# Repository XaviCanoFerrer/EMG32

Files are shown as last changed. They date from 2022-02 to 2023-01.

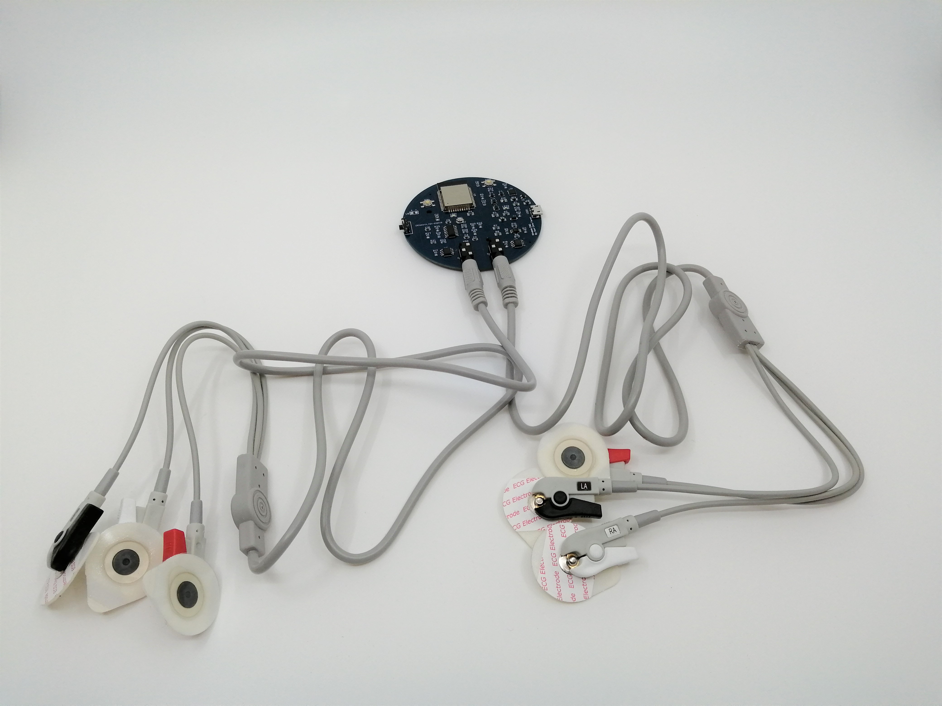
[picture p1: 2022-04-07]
IMG_20220404_123524.jpg

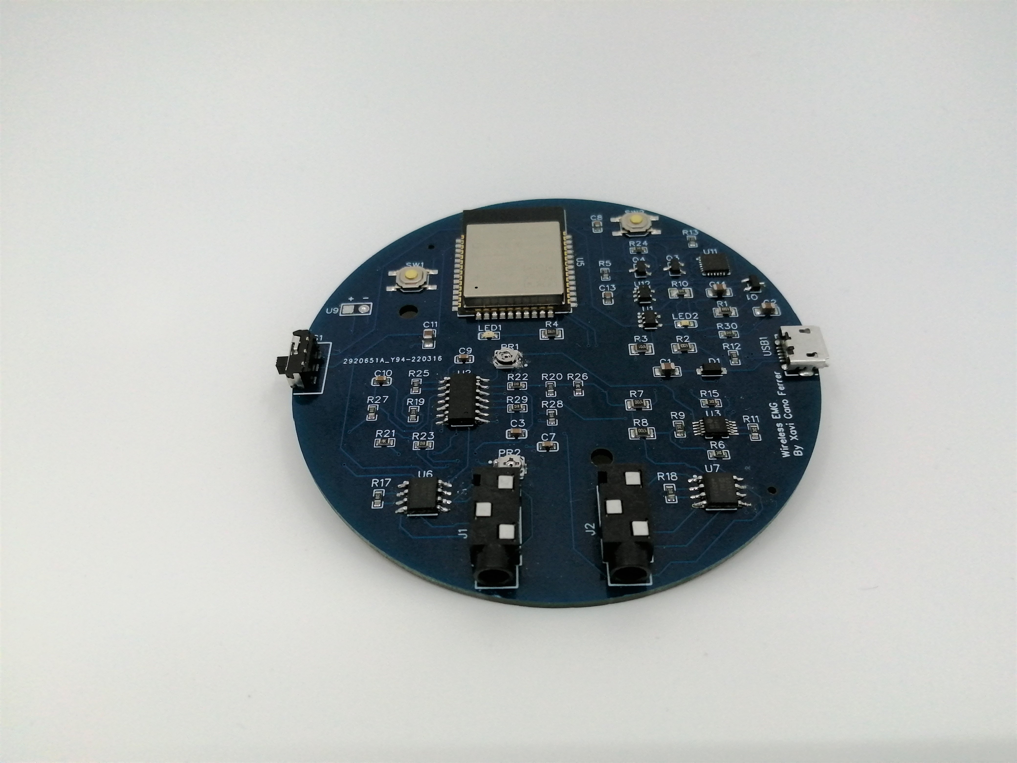
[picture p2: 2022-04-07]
IMG_20220404_123702.jpg

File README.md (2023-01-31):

# EMG32

Two-channel EMG acquisition system

# Features:

Adjustable total gain 100-10000

Instrumentation amplifier (AD8226)

12 bit ADC (Texas instruments ADS1015)

First order high and low pass filters fc = 22 Hz and fc = 482 Hz

LiPo battery power management system (It can be charged from the USB port)

The basic code has two modes, 2ch and 1 ch modes which can be selected pressing the SW1 pushbutton.

SW2 to reset the board.

Sampling frequencies 385 Hz through the serial port and 200 Hz using BT for 1 channel so not enough for sEMG standards Fs = 1kHz. 

It is still usable to measure muscle activity (RMS, how much and when) but not for frequency dependant processing or analysis as is shown in the single contraction spectrum:

<p align="center">
  
</p>

# V1 has a couple of mistakes but it can be fuctional: 

The quad amplifier (LM324) has to be assembled with a 180 degree rotation if not it will be shorted.

The JAC connectors are not close enough to the edge and depensing on the length of your cable it won't go deep enough to make a good contact.

Both mistakes are solved in V2.



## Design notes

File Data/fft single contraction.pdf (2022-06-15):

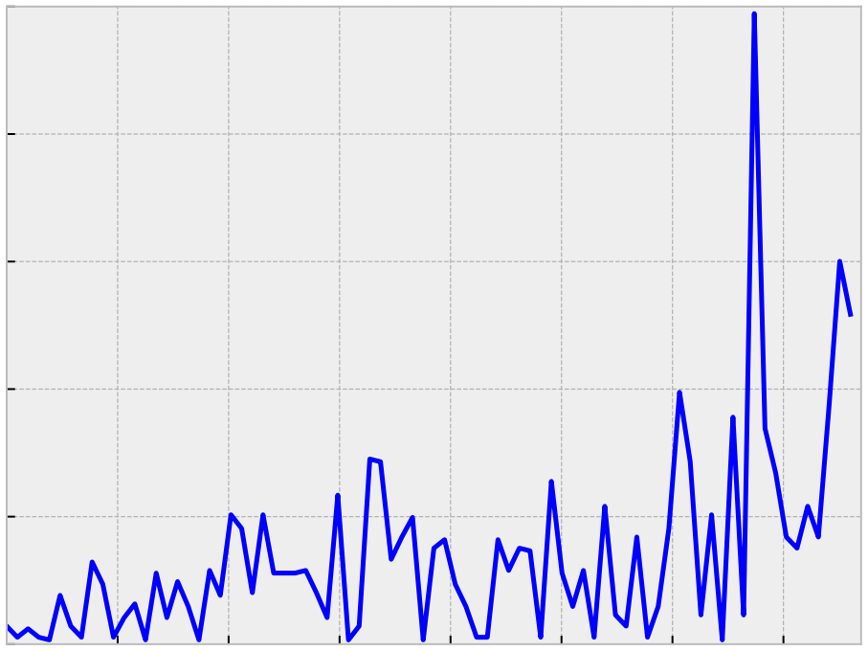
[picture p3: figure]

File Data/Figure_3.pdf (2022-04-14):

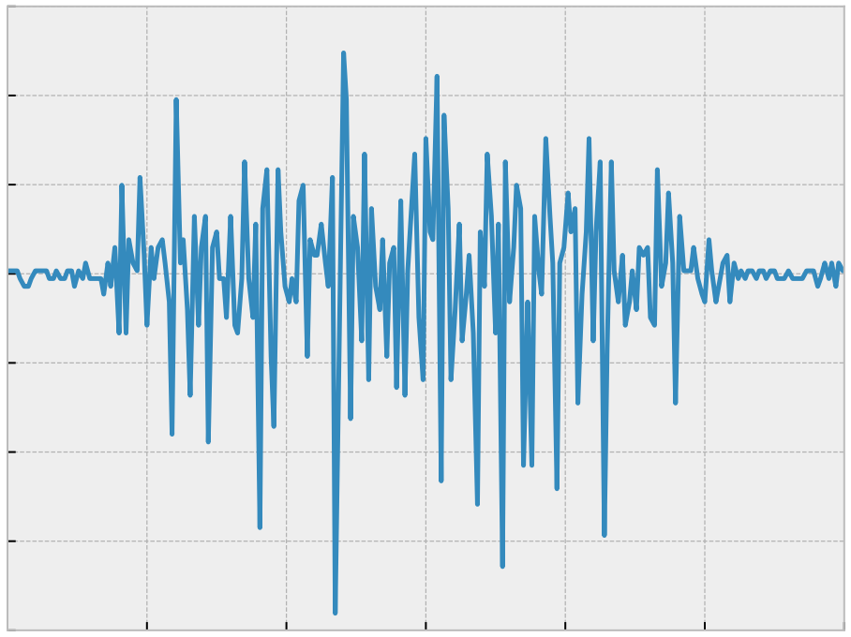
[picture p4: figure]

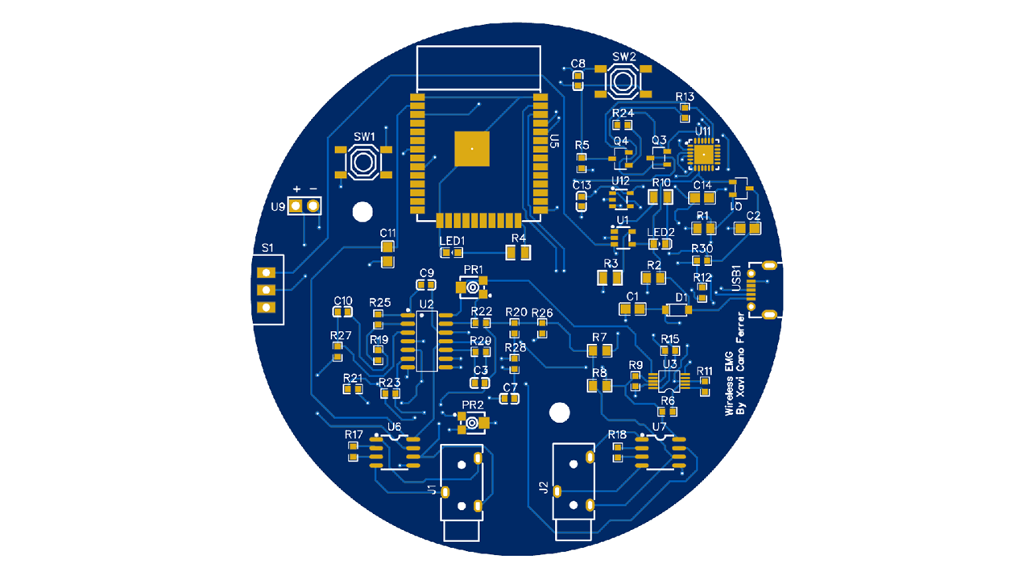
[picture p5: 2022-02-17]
Wireless EMG .png

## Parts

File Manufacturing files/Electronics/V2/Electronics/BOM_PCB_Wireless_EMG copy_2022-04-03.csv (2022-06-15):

ID | Name | Designator | Footprint | Quantity | Manufacturer Part | Manufacturer | Supplier | Supplier Part | Price | JLCPCB Part Class | LCSC Assembly
1 | LED-0603_G | LED1 | LED0603_GREEN | 1 | 0805G (Green) | KENTO | LCSC | C2297
2 | LM324 | U2 | SOIC-14_L8.7-W3.9-P1.27-LS6.0-BL | 1 | LM324 | PUOLOP | LCSC | C351427 | 0.143 | Extended Part
3 | AP7365-33WG-7 | U4 | SOT-25_L3.0-W1.6-P0.95-LS2.8-BR | 1 | AP7365-33WG-7 | DIODES | LCSC | C150742 | 0.229 | Extended Part
4 | 0.33uF | C3,C10 | C0603 | 2 | 0603B334K250NT | FH | LCSC | C1615 | 0.012
5 | 0.47uF | C7,C9 | C0603 | 2 | CL10B474KA8NNNC | SAMSUNG | LCSC | C1623 | 0.007
6 | 1uF | C8,C13 | C0603 | 2 | CL10A105KB8NNNC | SAMSUNG | LCSC | C15849 | 0.005
7 | 100 | R4 | R0805 | 1 | RC0805JR-07100RL | YAGEO | LCSC | C106949 | 0.002 |  | Yes
8 | 270 | R10 | R0805 | 1 | 0805W8F2700T5E | UniOhm | LCSC | C17590 | 0.003 |  | Yes
9 | 10uF | C1,C2,C14,C11 | C0805 | 4 | CL21A106KAYNNNE | SAMSUNG | LCSC | C15850 |  | Basic Part
10 | MBR120LSF | D1 | SOD-123_L2.8-W1.8-LS3.7-RD | 1 | MBR120LSF | SK | LCSC | C130880 | 0.035 | Extended Part
11 | Black headphone jack | J1,J2 | AUDIO-TH_PJ-3200 | 2 | Black headphone jack | BOOMELE | LCSC | C18166 | 0.049 | Extended Part
12 | LED-0603_R | LED2 | LED0603_RED | 1 | FC-2012HRK-620D | NATIONSTAR | LCSC | C84256 | 0.014
13 | 100K | PR1,PR2 | RES-ADJ-SMD_EVM3ESX50B25 | 2 | 0603WAF1003T5E | UniOhm | LCSC | C25803 | 0.001 | Extended Part
14 | DMG3415UQ-7 | Q1 | SOT-23-3_L2.9-W1.6-P1.90-LS2.8-BR | 1 | DMG3415U-7 | Diodes Incorporated | LCSC | C96616 | 0.666 | Extended Part
15 | MMBT2222A-G | Q3,Q4 | SOT-23-3_L2.9-W1.6-P1.90-LS2.8-BR | 2 | MMBT2222A-G | CJ | LCSC | C164898 | 0.021 | Extended Part
16 | 100K | R1,R2 | R0805 | 2 | RC0805FR-07100KL | YAGEO | LCSC | C96346 | 0.003 | Basic Part
17 | 470R | R7,R8 | R0805 | 2 | 0805W8F4700T5E | UniOhm | LCSC | C17710 | 0.002 | Basic Part
18 | 4.7k | R3 | R0805 | 1 | RMC08054.7K1%N | Tyohm | LCSC | C269746 | 0.006 |  | Yes
19 | 10k | R5,R6,R9,R11,R13,R15,R24 | R0603 | 7 | RMC060310K1%N | Tyohm | LCSC | C269701 | 0.004
20 | 100k | R12,R30 | R0603 | 2 | 0603WAF1003T5E | UniOhm | LCSC | C25803 | 0.001
21 | 1k | R17,R18,R19,R20,R22,R23,R25,R27,R28,R29 | R0603 | 10 | 0603WAF1001T5E | UniOhm | LCSC | C21190 | 0.001
22 | 15k | R21,R26 | R0603 | 2 | CR0603FA1502G | LIZ | LCSC | C100780 | 0.001
23 | TL32PO | S1 | TL3XPO | 1
24 | TS-1187A-B-A-B | SW2,SW1 | SW-SMD_4P-L5.1-W5.1-P3.70-LS6.5-TL-2 | 2 | TS-1187A-B-A-B | XKB Enterprise | LCSC | C318884 | 0.016 | Extended Part
25 | MCP73831T-2ACI/OT | U1 | SOT-23-5_L3.0-W1.7-P0.95-LS2.8-BR | 1 | MCP73831T-2ACI/OT | Microchip Tech | LCSC | C424093 | 0.949 | Extended Part
26 | ADS1015QDGSRQ1 | U3 | VSSOP-10_L3.0-W3.0-P0.50-LS4.9-BL | 1 | ADS1015QDGSRQ1 | Texas Instruments | LCSC | C201686 | 3.652 | Extended Part
27 | ESP32-WROOM-32D(16MB) | U5 | WIFIM-SMD_39P-L25.5-W18.0-P1.27-BL | 1 | ESP32-WROOM-32D | ESPRESSIF 乐鑫 | LCSC | C473012 | 3.751 | Extended Part
28 | AD8226ARZ | U6,U7 | SOIC-8_L5.0-W4.0-P1.27-LS6.0-BL | 2 | AD8226ARZ | ADI | LCSC | C34250 | 4.68 | Extended Part
29 | CP2104-F03-GM | U11 | QFN-24_L4.0-W4.0-P0.50-BL-EP2.7 | 1 | CP2104-F03-GM | SILICON LABS | LCSC | C47742 | 4.169 | Basic Part
30 | micro USBFemale | USB1 | MICRO-USB-SMD_5P-P0.65-H-F_C10418 | 1 | micro USBFemale | ValuePro | LCSC | C10418 | 0.065 | Extended Part
31 | 54102-T0600LF | U9 | HDR-TH_2P-P2.54-V-M-R2-C1-S2.54 | 1 | 54102-T0600LF | Amphenol ICC | LCSC | C213465 | 0.018

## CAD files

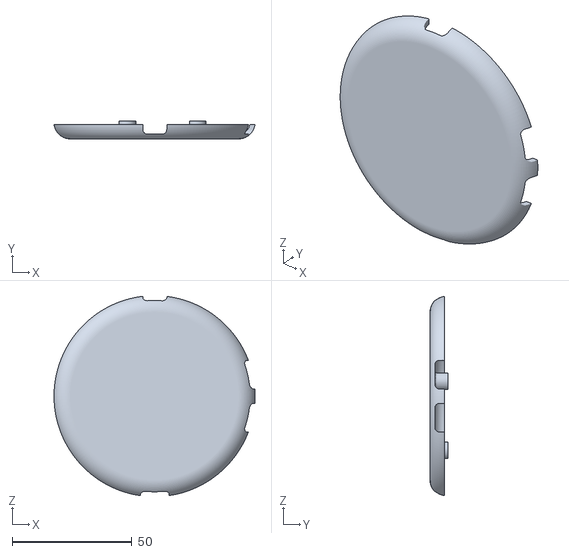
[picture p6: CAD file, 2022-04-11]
Manufacturing files/Case/Case top (Without holes for LED).stl
84.0 x 7.50 x 83.3

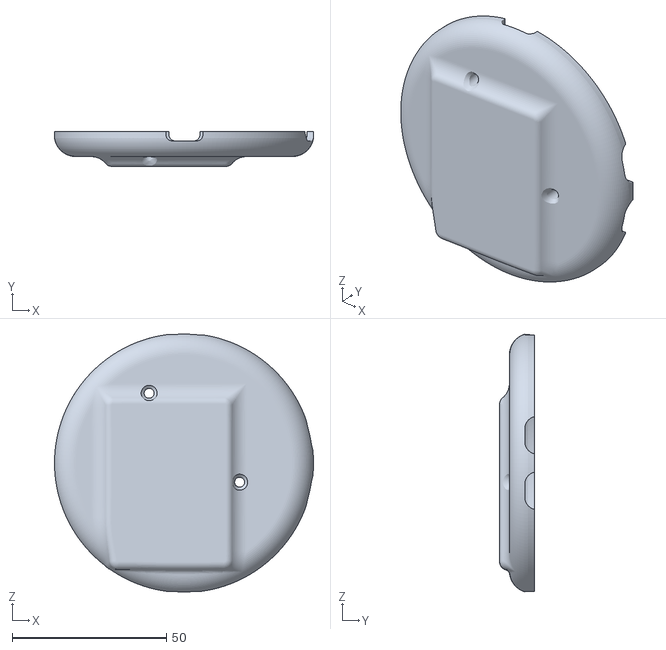
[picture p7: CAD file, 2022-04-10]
Manufacturing files/Case/Case bottom V2.stl
84.0 x 11.3 x 83.6

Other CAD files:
Manufacturing files/Case/Case top.stl
Design files/Case/Case assembly.iam
Design files/Case/Case bottom V2.ipt
Design files/Case/Case bottom.ipt
Design files/Case/Case top.ipt
Design files/Case/OldVersions/Case assembly.0003.iam
Design files/Case/OldVersions/Case top.0010.ipt
Design files/OldVersions/Case assembly.0002.iam
Design files/OldVersions/Case bottom V2.0009.ipt
Design files/OldVersions/Case bottom.0009.ipt
Design files/OldVersions/Case top.0009.ipt

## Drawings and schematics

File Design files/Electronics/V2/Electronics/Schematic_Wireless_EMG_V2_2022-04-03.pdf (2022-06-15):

## Power supply

## USB to serial converter

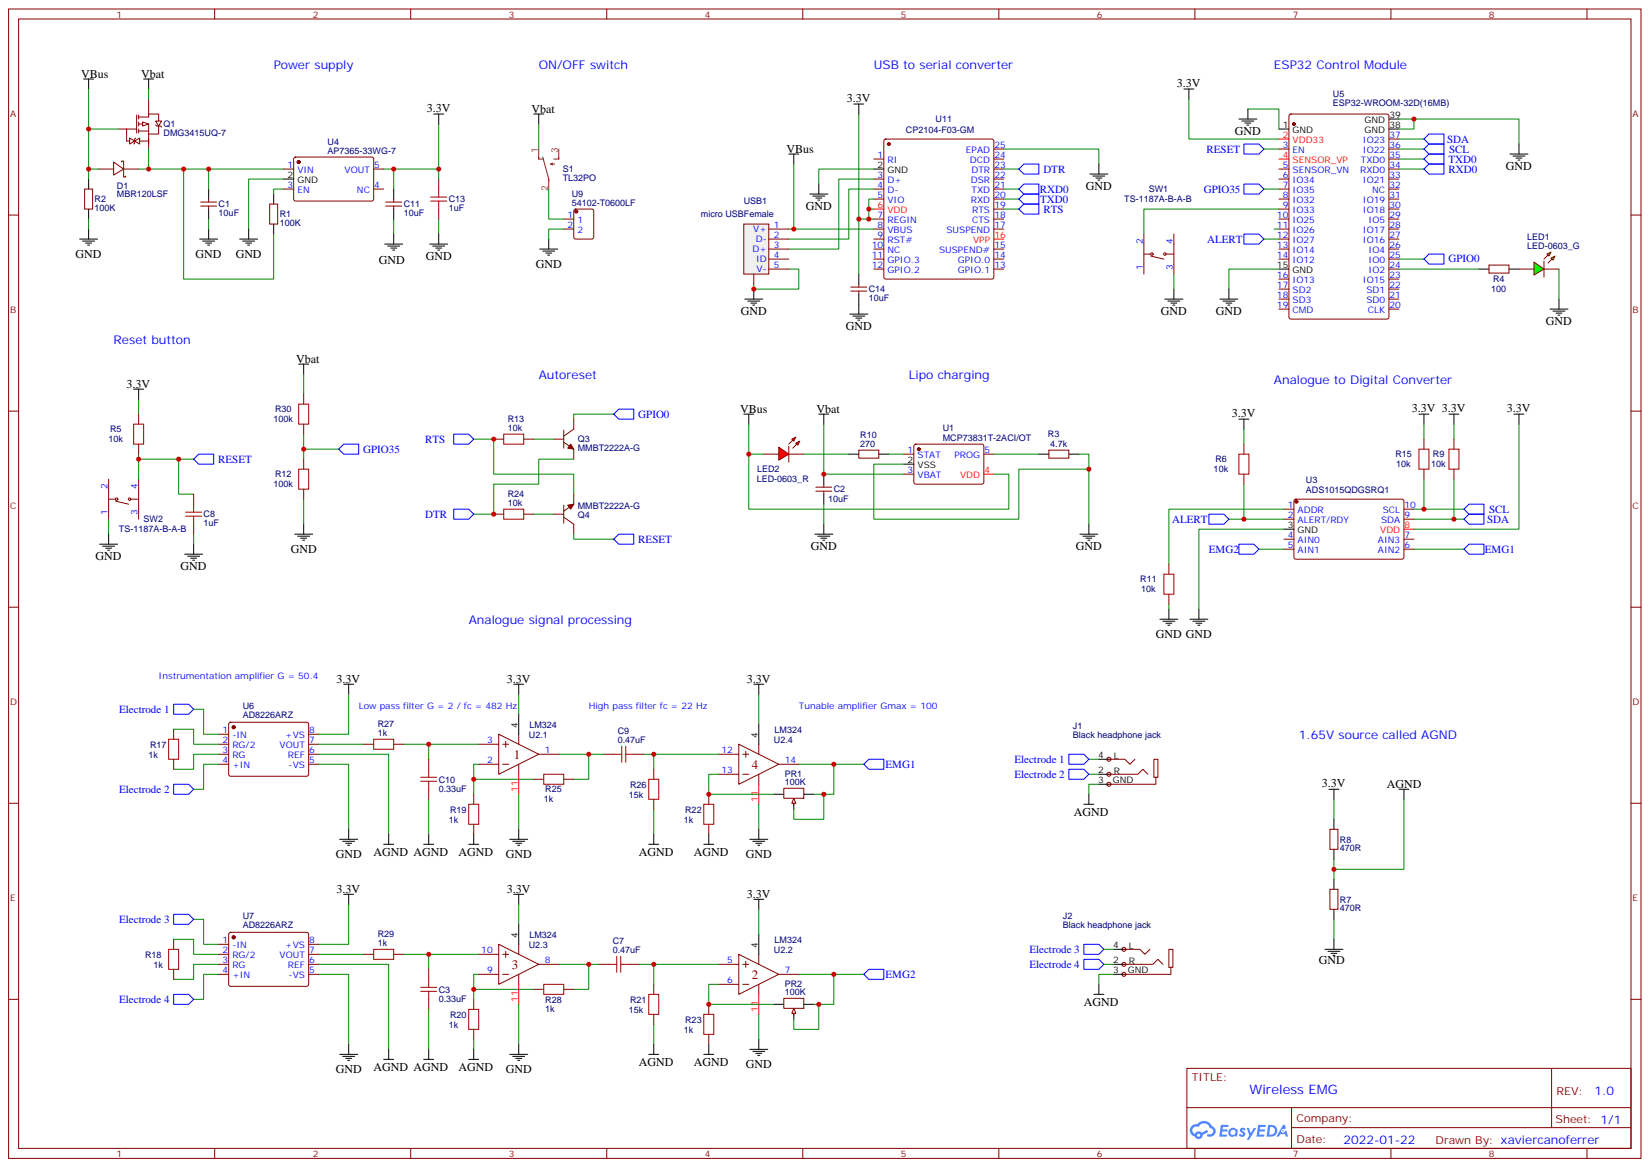
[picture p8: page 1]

Analogue to Digital Converter Lipo charging

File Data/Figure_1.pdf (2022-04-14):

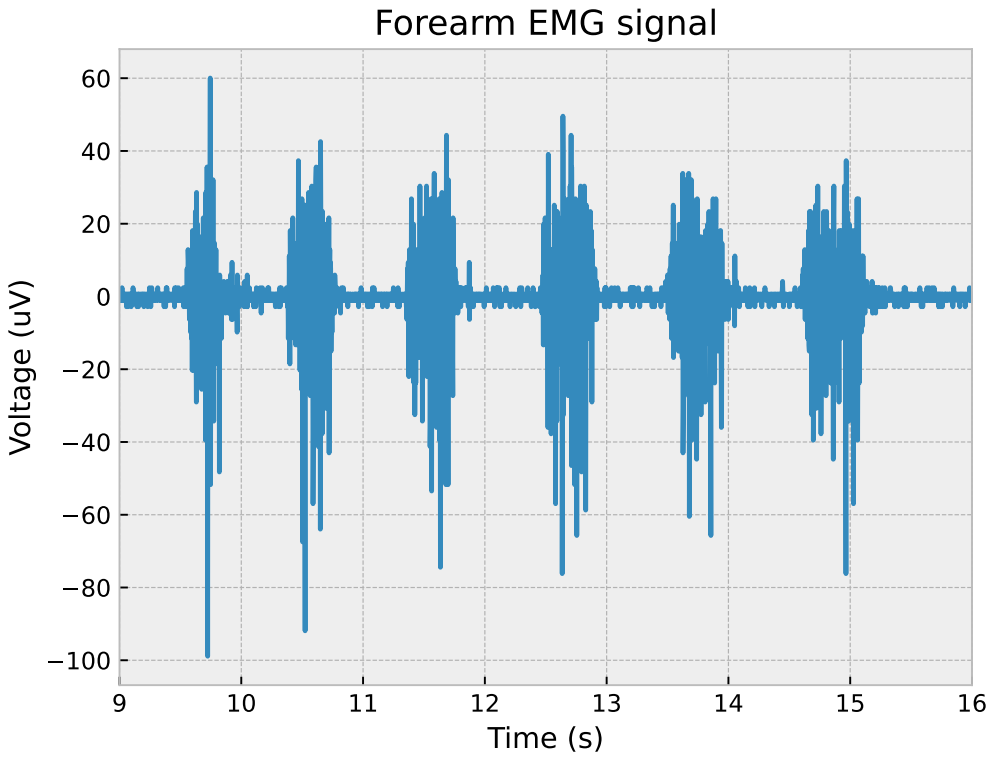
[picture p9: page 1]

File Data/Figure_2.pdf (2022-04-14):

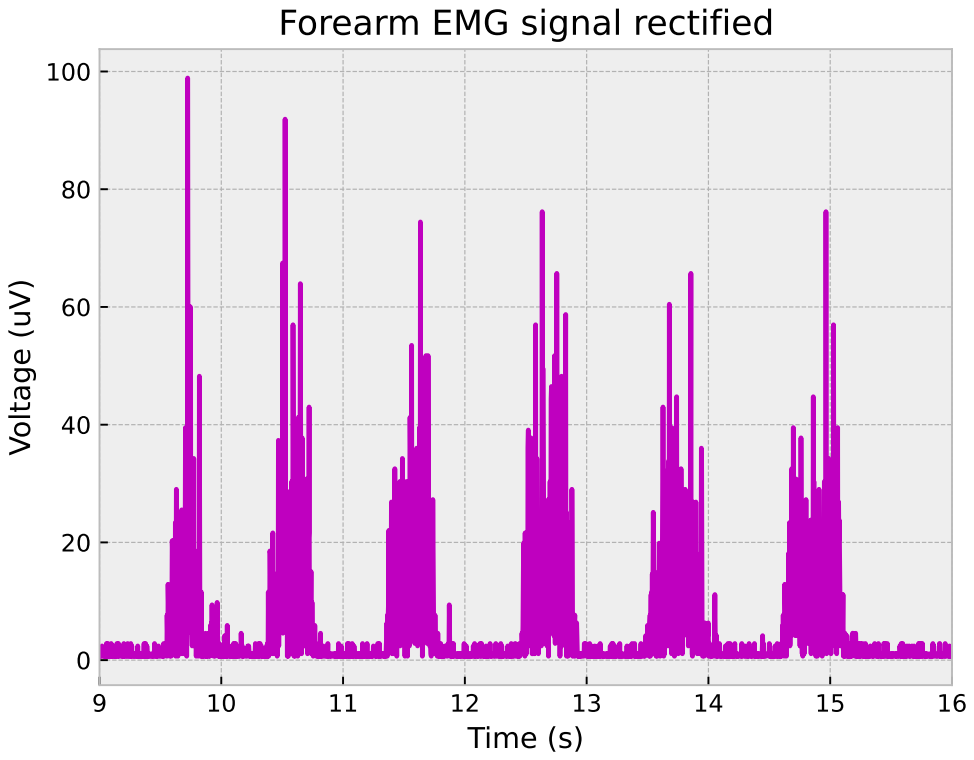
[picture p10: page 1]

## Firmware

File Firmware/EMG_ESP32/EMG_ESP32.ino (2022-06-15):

/*
  ----------------------------------------------------------------------------
  This file is part of the EMG32 repository
  Written by Xavier Cano-Ferrer
  ----------------------------------------------------------------------------
  This program is free software: you can redistribute it and/or modify
  it under the terms of the GNU General Public License as published by
  the Free Software Foundation, version 3.
  This program is distributed  WITHOUT ANY WARRANTY and without even the
  implied warranty of MERCHANTABILITY or FITNESS FOR A PARTICULAR PURPOSE.
  See the GNU General Public License for more details.
  You should have received a copy of the GNU General Public License
  along with this program.  If not, see <http://www.gnu.org/licenses/>.
*/

#include <Adafruit_ADS1X15.h>

Adafruit_ADS1015 ads;     /* Use this for the 12-bit ADC version */

const int LED_pin = 2;
const int button_pin = 33;
bool state = 1;
bool parallax = false; // True if you want to acquire with Parallax PLX-DAQ
int16_t ch1, ch2;
float volts1, volts2;

void setup(void) 
{
  //Serial.begin(256000); // Fastest Baud rate for Parallax PLX-DAQ
  Serial.begin(2000000);
  //To transmit in Parallax PLX-DAQ
  Serial.println("CLEARDATA");
  Serial.println("LABEL,Realtime,EMG_ch1, EMG_ch2,Time(ms)");

  pinMode(LED_pin, OUTPUT);
  pinMode(button_pin, INPUT_PULLUP);

  digitalWrite(LED_pin, state);

  // The Interrupt calls the function _mode
  attachInterrupt(digitalPinToInterrupt(button_pin), _mode, FALLING);
  
  // The ADC input range (or gain) can be changed via the following
  // functions, but be careful never to exceed VDD +0.3V max, or to
  // exceed the upper and lower limits if you adjust the input range!
  // Setting these values incorrectly may destroy your ADC!
  //                                                                ADS1015  ADS1115
  //                                                                -------  -------
   //ads.setGain(GAIN_TWOTHIRDS);  // 2/3x gain +/- 6.144V  1 bit = 3mV      0.1875mV (default)
   ads.setGain(GAIN_ONE);        // 1x gain   +/- 4.096V  1 bit = 2mV      0.125mV
  // ads.setGain(GAIN_TWO);        // 2x gain   +/- 2.048V  1 bit = 1mV      0.0625mV
  // ads.setGain(GAIN_FOUR);       // 4x gain   +/- 1.024V  1 bit = 0.5mV    0.03125mV
  // ads.setGain(GAIN_EIGHT);      // 8x gain   +/- 0.512V  1 bit = 0.25mV   0.015625mV
  // ads.setGain(GAIN_SIXTEEN);    // 16x gain  +/- 0.256V  1 bit = 0.125mV  0.0078125mV
  
  Wire.setClock(400000);
  ads.setDataRate(RATE_ADS1015_3300SPS); // Fastes sampling rate possible on the ADC
  ads.begin();
  //delay(1000);

}

void loop(void) 
{
  digitalWrite(LED_pin, state);
  
  // unsigned long start = micros();
  if (state == 1)
  {
    // Read the two ADC channels
    ch2 = ads.readADC_SingleEnded(1);
    ch1 = ads.readADC_SingleEnded(2);

    // Convert the 12 bit data into volts
    volts1 = ads.computeVolts(ch1);
    volts2 = ads.computeVolts(ch2);

    if (parallax == true)
    {
      //To transmit in Parallax PLX-DAQ
      Serial_Parallax_PLX_DAQ();
    }
    else 
    {
      //Regular serial print
      _print();
    }
  }
  if (state == 0)
  {
    // Read only channel 1
    ch1 = ads.readADC_SingleEnded(2);

    // Convert the 12 bit data into volts
    volts1 = ads.computeVolts(ch1);

    if (parallax == true)
    {
      //To transmit in Parallax PLX-DAQ
      Serial_Parallax_PLX_DAQ_1ch();
    }
    else 
    {
      //Regular serial print
      _print_1ch();
    }
  }
}

void Serial_Parallax_PLX_DAQ()
{
  Serial.print("DATA,TIME,");
  Serial.print(volts1);
  Serial.print(","); 
  Serial.print(volts2);
  Serial.print(","); 
  Serial.println(millis());
}

void Serial_Parallax_PLX_DAQ_1ch()
{
  Serial.print("DATA,TIME,");
  Serial.print(volts1);
  Serial.print(","); 
  Serial.println(millis());
}

void _print()
{
  Serial.print(volts1);
  Serial.print(" "); 
  Serial.print(volts2);
  Serial.print(" "); 
  Serial.println(millis());
}

void _print_1ch()
{
  Serial.print(volts1);
  Serial.print(" "); 
  Serial.println(millis());
}

void _mode()
{
  state = !state;
}

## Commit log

2022-04-02 data 1
    [Wireless EMG data 1.xlsx]
2022-04-06 Data figures
    [Wireless EMG data 1.xlsx]
2022-04-07 Case 1
    [Case bottom.0001.ipt, Case bottom.ipt, Case top.0001.ipt, Case top.ipt]
2022-04-10 case 2
    [BOM_PCB_Wireless_EMG copy_2022-04-03.csv, BOM_PCB_Wireless_EMG_2022-02-08.csv, Case assembly.0002.iam, Case assembly.iam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]
2022-04-11 Case 3
    [Case assembly.0003.iam, Case assembly.iam, Case top (Without holes for LED).stl, Case top.0010.ipt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]
2022-04-12 EOG data
    [EOG1.xlsx]
2022-04-13 EMG data 2
    [EMG2.xlsx]
2022-06-15 Schematic V2
    [BOM_PCB_Wireless_EMG copy_2022-04-03.csv, PickAndPlace_PCB_Wireless_EMG copy_2022-04-03.csv]
